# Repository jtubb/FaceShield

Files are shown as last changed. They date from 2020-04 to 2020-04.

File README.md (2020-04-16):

# FaceShield

Rapid prototype face shield for front line medical workers. The goal was to develop a face shield that could be made quickly with materials not traditionally being consumed by other Covid-19 response efforts, easy to sanitize/replace parts, and keeping the price point under $5 per unit. When you're done you'll have a mold that can make ~25 visors in 15 minutes, timing the pours correctly you can cast them continuously. The mold can be reused thousands of times.

This project is released under the Creative Commons Zero Universal license. You may do whatever you like with these designs, my advice is work closely with the medical workers you will provide these too to make sure they are being used appropriately.

For a quick video overview see: https://youtu.be/5g29kG8YU5k

# Tools

80W+ Laser Cutter with minimum 20"x20" bed, or printer+jigsaw.

Table saw, or circular saw, or jigsaw, or handsaw.

Mixing pot - Cheap stainless steel pot

Mixing utensil - I used a cheap silicon spatula

# Software

DeepNest.IO - https://github.com/Jack000/Deepnest

# Materials

2 - 2'x4' 1/4" MDF Sheets from Home Depot - $6.50 ea

1 - Wood Glue - $5

1 - Spray on polyurethane - $7

1 - Silicon Caulking - $5

1 - Silicon Spray - $7

1 - EasyFlo 60 76 LB Kit - $461.00 (https://www.polytek.com/products/easyflo-60-liquid-plastic)

1 - PlatSil 70-71 16 LB Kit - $286.00 (https://www.polytek.com/products/platsil-71-11-silicone-rubber)

7 - 75ft 1/4" PVC self adhesive foam - $7 ea

800 - A4 PVC Sheets - $35 200pc (I used Fellowes Crystals Clear PVC Binding Covers, 8mil Letter, 200 Pack (5204303))

1000 - Elastic Straps (I am using rubber bands, other alternatives include hair bands, leggings cut to bands, string, shoelaces, etc)

Total cost ~$1000 + ~$80 Shipping of the material from polytex.

The large cast takes ~2oz of resin. With 10 gallons of EasyFlow you'll get ~640 masks. 
Price per unit $1080/640 = $1.69

Once the mold is made each additional batch of 640 visors is only material costs. EasyFlo 60 + A4 PVC Sheet + Elastic Straps + PVC foam = ~$730

Price per unit Batch 2 $1810/1240 = $1.45

Price per unit Batch 3 $2540/1860 = $1.36

Price per unit Batch 4 $3270/2480 = $1.32

You can also gain more efficiency by using the blank to create more than one mold.

# Directions

If your laser bed is 20" square you can skip to Step 2 and just use the "20InchBedOptimizedLayout.dxf"

Step 1. Import the various sizes of Faceshield DXF into DeepNest. The only setting I changed was to increase Part Rotations to 16 and clearance to 4mm. Set a bounding box appropriate for your laser bed.

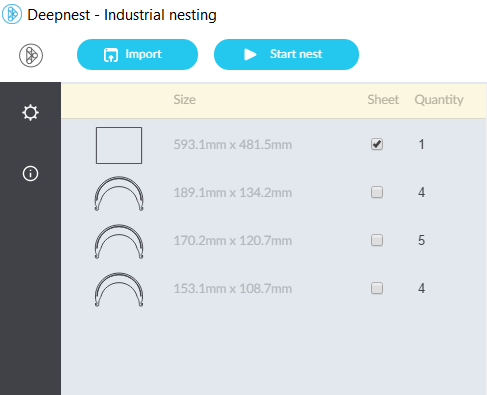
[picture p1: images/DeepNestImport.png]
Import


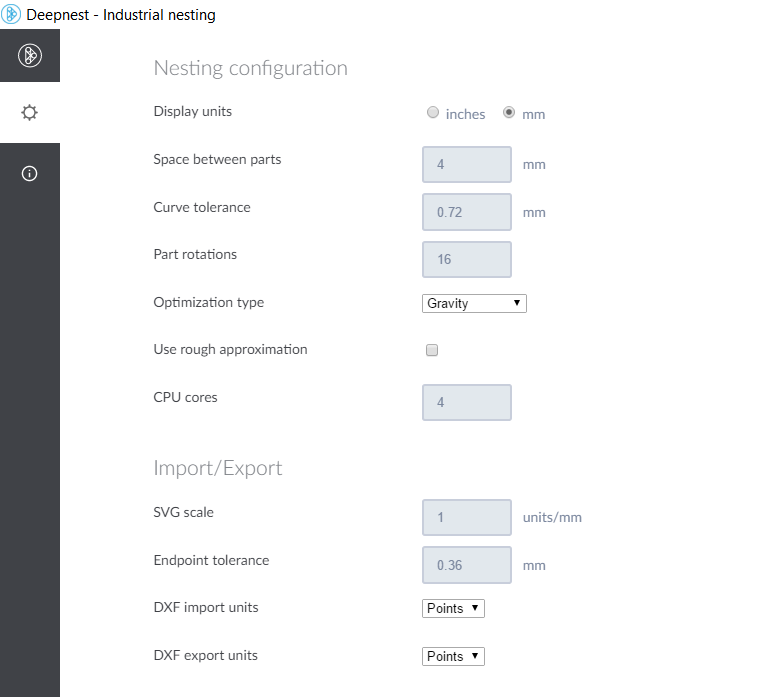
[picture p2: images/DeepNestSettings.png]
Settings


Step 2. Pull the optimized part layout into your laser cutting software of choice, I use LightBurn. Begin the cut. For MDF my speed+feed for an 80W laser is 7mm/s at 40%power.

Step 2a. If you do not have access to a laser cutter, you can also print the DXF as a template, glue it to the MDF, and cut it out with a jigsaw.

Step 3. Sand any sharp edges and make sure the visor channel is cleared of all debris.

Step 4. Glue all blanks that were just cut out to the second 2'x4' sheet of MDF using standard wood glue, you should be able to fit at least 25 blanks. Wipe up any excess glue. Make sure to keep the pieces centered on the sheet of MDF.

Step 5. Trim 1" of material from each edge of the 2'x4' with the blanks glued to it. Make sure there is at least a 1/4" between any blank and the edge after cutting.

Step 6. Using some 1" square scrap pieces of wood, use wood glue to fix the 1" MDF strips from Step 5 to create a lip around the 2'x4' MDF sheet.

Step 7. Once the glue has dried apply silicon caulk to the lip where it meets the 2'x4' MDF sheet. This will prevent any leaks and provide extra holding for the lip.

Step 8. Once the silicon has dried ensure the mold is clean of any debris, and then coat the mold with polyurethane spray. Makes sure to spray from all angles.

Step 9. Once the first coat of polyurethane has dried apply a second coat.

Step 10. Once the second coat of polyurethane has dried apply a coat of spray silicon. Make sure to spray from all angles. Wipe up any puddling.

Step 11. Make sure the mold is leveled and on a flat surface. I recommend putting a plastic sheet under it in case there are any leaks.

Step 12. Mix the PlatSil 70-71 per the manufacture instructions. The material is fairly sticky and mixing was done best in a stainless steel container with a rubber spatula. Once cured any excess can be easily peeled off the mixing tools.

Step 13. Pour the mold material into the center of the mold blank. Use the spatula evenly spread the mold material to the edges of the mold blank. If you have a palm sander or another tool that shakes quite a bit run it along the edges of the mold or the surface the mold is on to vibrate any trapped air bubbles out. Monitor the level of the mold blank for the first 20 minutes to make sure it is level and won't overflow.

Step 14. Let sit approximately 24 hours. I demolded after 14 hours and the let it continue to cure for the other 10 hours. If you plan to make more molds be careful to not damage the blanks when removing, repeat steps 10 through 14 for each mold. The blank should hold up well enough to make 4 or 5 molds.

Step 15. Clean the mold of any debris and ensure it is level.

Step 16. Prepare the EasyFlo 60 per manufacture instructions. It only has a 2 minute work time. I delt with this by having a pint container of part A and a separate container of part B on my workspace. I added 3oz of part A and part B to my mix pot, stir for 15 seconds until the mix went clear, then pour into the mold. That was enough to fill ~3 visors. I repeated this until all molds were filled. I was pouring in a cold basement so I used a heat gun on low to help cure the material, a hair dryer would work just a well.

Step 17. Demold per the manufacture instructions. It took approximately 15 minutes for the pieces to be cured enough to remove, be gentle as they will still be a little soft.

Step 18. Let demolded pieces harden per manufacture instructions. Approximately 2 hours.

Step 19. Sand the top side of the cast visors if necessary.

Step 20. Apply approx 8" of 1/4" foam to the inside brim of the visor.

Step 21. Insert PVC shield material into the visor channel.

Step 22. Attach elastic bands to the ear pieces and begin fitting the visor.

# Shield Material

I used a length of nichrome wire run between 2 hinged boards to make a simple plastic bender. Anything that can heat the A4 PVC material to ~140-150 degF can be used. See the Plastic Folder directory for a simple arduino temperature controller and designs for the folder.

From the landscape (hotdog) orientation, I created a 1/4" fold on the left and right side of the A4 PVC sheet. This will provide rigid edges for the mask. If using a small visor make a 1/2" fold on each side. Then on the top edge make a 90deg bend.

Alternatively if you don't want to bend the PVC you can apply staples along the top edge of the sheet.

# Use and Sanitization

Don the face shield per CDC recommendation (https://www.cdc.gov/vhf/ebola/hcp/ppe-training/n95respirator_gown/donning_13.html).

If made with a urethane resin the visor can be sanitized in an autoclave, the foam strip will need to be removed for this.

If sanitizing with O2 the entire assembly can be placed in the sanitization chamber.

Elastic bands should be replaced every use.

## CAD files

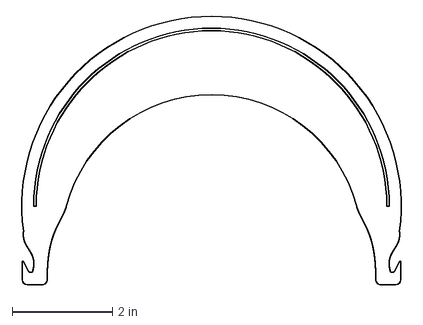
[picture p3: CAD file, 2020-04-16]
Facemask v3.dxf
7.81 x 5.37 in

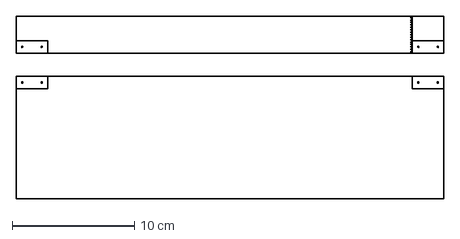
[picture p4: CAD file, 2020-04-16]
PlasticFolder/Folderv1.dxf
35.0 x 14.9 cm

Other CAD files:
Facemask v3.f3d
PlasticFolder/Folder v1.f3d

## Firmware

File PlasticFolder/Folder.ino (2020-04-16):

#include <AutoPID.h>
#include <Wire.h> // Enable this line if using Arduino Uno, Mega, etc.
#include <Adafruit_GFX.h>
#include "Adafruit_LEDBackpack.h"

// which analog pin to connect
#define THERMISTORPIN A0
// resistance at 25 degrees C
#define THERMISTORNOMINAL 100000
// temp. for nominal resistance (almost always 25 C)
#define TEMPERATURENOMINAL 25
// how many samples to take and average, more takes longer
// but is more 'smooth'
#define NUMSAMPLES 5
// The beta coefficient of the thermistor (usually 3000-4000)
#define BCOEFFICIENT 3950
// the value of the 'other' resistor
#define SERIESRESISTOR 10000

//pid settings and gains
#define WINDOWSIZE 1000
#define KP .12
#define KI .0003
#define KD 0

#define OUTPUT_PIN 2

double temperature;
double setPoint = 130.0;
bool outputVal;

//input/output variables passed by reference, so they are updated automatically
AutoPIDRelay myPID(&temperature, &setPoint, &outputVal, WINDOWSIZE, KP, KI, KD);

Adafruit_7segment matrix = Adafruit_7segment();

int samples[NUMSAMPLES];

void setup(void) {
  Serial.begin(9600);
  analogReference(EXTERNAL);
  pinMode(OUTPUT_PIN, OUTPUT);
  digitalWrite(OUTPUT_PIN, LOW);

  //if temperature is more than 4 degrees below or above setpoint, OUTPUT will be set to min or max respectively
  myPID.setBangBang(1);
  //set PID update interval to 4000ms
  myPID.setTimeStep(1000);

  matrix.begin(0x70);
}

void loop(void) {
  uint8_t i;
  float average;

  // take N samples in a row, with a slight delay
  for (i = 0; i < NUMSAMPLES; i++) {
    samples[i] = analogRead(THERMISTORPIN);
    delay(10);
  }

  // average all the samples out
  average = 0;
  for (i = 0; i < NUMSAMPLES; i++) {
    average += samples[i];
  }
  average /= NUMSAMPLES;

  Serial.print("Average analog reading ");
  Serial.println(average);

  // convert the value to resistance
  average = 1023 / average - 1;
  average = SERIESRESISTOR / average;
  Serial.print("Thermistor resistance ");
  Serial.println(average);

  float steinhart;
  steinhart = average / THERMISTORNOMINAL;     // (R/Ro)
  steinhart = log(steinhart);                  // ln(R/Ro)
  steinhart /= BCOEFFICIENT;                   // 1/B * ln(R/Ro)
  steinhart += 1.0 / (TEMPERATURENOMINAL + 273.15); // + (1/To)
  steinhart = 1.0 / steinhart;                 // Invert
  steinhart -= 273.15;                         // convert to C

  temperature = steinhart * 1.8 + 32;
  Serial.print("Temperature ");
  Serial.print(temperature);
  Serial.println(" *F");
  matrix.print(temperature);
  matrix.writeDisplay();

  myPID.run();
  digitalWrite(OUTPUT_PIN, outputVal);
  
  delay(1000);
}
